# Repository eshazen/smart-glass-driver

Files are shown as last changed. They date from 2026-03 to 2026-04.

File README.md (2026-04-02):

# smart-glass-driver

This is a line-powered programmable function generator capable
of generating an output of about 140V pk-pk on each of two outputs
(which can be out of phase).

Here are the specs from Darren:

1.  Provide amplitude up to about 60-70Vpp AC (note: not 60 VAC RMS),
    we need to be able to change the amplitude for testing, with
    likely voltages 20, 30, 40, 50, 60 VppAC
2.  We also need to be able to alter the AC frequency, from low Hz to
    up to at least 1 kHz.
3.  We need to be able to have control over the output, with the
    ability to modulate (binary turn on and off) the output signal
    from a few Hz to up to about 300Hz. We would use this for
    lock-in. I envision control with a digital I/O pin.

For 1kHz sine wave with ~16 samples per cycle, the sampling rate would
be 62.5us or for 8 samples 125us.  

We need to stop Timer0 to avoid the interrupts.  Use TimerOne library
to interrupt at 62us and take values from a table.  This seems to
work just fine.  **But** we need to do two channels
out of phase on two DACs.  Simulate this with Set1 and Set2 functions.

The slew rate of the LTC6090 is spec'd at 21V/us.  So for 120V this
would be about 6uS or a minimum cycle time of 12uS 80kHz so no problem
reproducing a 1kHz output.  This is well matched to the 5us slew of
the DAC.

## 2026-04-02

ECOs for "Eric's" board:

*  Solder a wire between pins 1 and 6 of U1 (best done on the bottom side)
This connects DAC reference to 5V
*  Solder a wire between J4 pin 3 and J2 pin 5
*  Solder a wire between J4 pin 4 and J2 pin 7.
This connects the SPI data and clock to the right Arduino pins

## 2026-04-01

Ordered parts to assemble a system based on a transformer-based zener supply
and two InTENS shield boards.

Investigating the MCP492x DAC using the BE511 shield board.
<br>DAC setting code for first test:

```
    // Write a word to DAC channel 0 only
    // Unbuffered mode so no need to manipulate LDAC
    void MCP4922::Set1( int A) {
      int channelA = A | 0b0011000000000000; // unbuffered mode, gain = 2X
      SPI.beginTransaction(SPISettings(MCP_CLOCK, MSBFIRST, SPI_MODE0));
      digitalWrite(_CS, LOW);
      SPI.transfer(highByte(channelA));
      SPI.transfer(lowByte(channelA));
      digitalWrite(_CS, HIGH);
      SPI.endTransaction();
    }
```

On an Uno R3 with SPI clk set to 8MHz this takes 17us (plus any timer
interrupt delay).  Also the DAC takes 5us to slew full scale (roughly
linear).

**Software Written**: sketch `DAC_Function_Gen` accepts integer rates
from 25-2000 Hz (more or less, up to 1kHz best).  Serial at 9600.

## 2026-03-31

### Testing the commercial setup

Made some measurements of the commercial driver with Weizhe.
General observations:

* Drive electronics supplied provides about 200V pk-pk AC
two-phase at 60Hz.  Not quite sinusoidal.
* Tested with 4.7k resistor in series.  Current waveform
is roughly in phase with voltage.  Amplitude is about 2mA (absolute value).

### Testing Amazon HV supply

Now testing an HV supply I found in the box with the InTENS stuff.

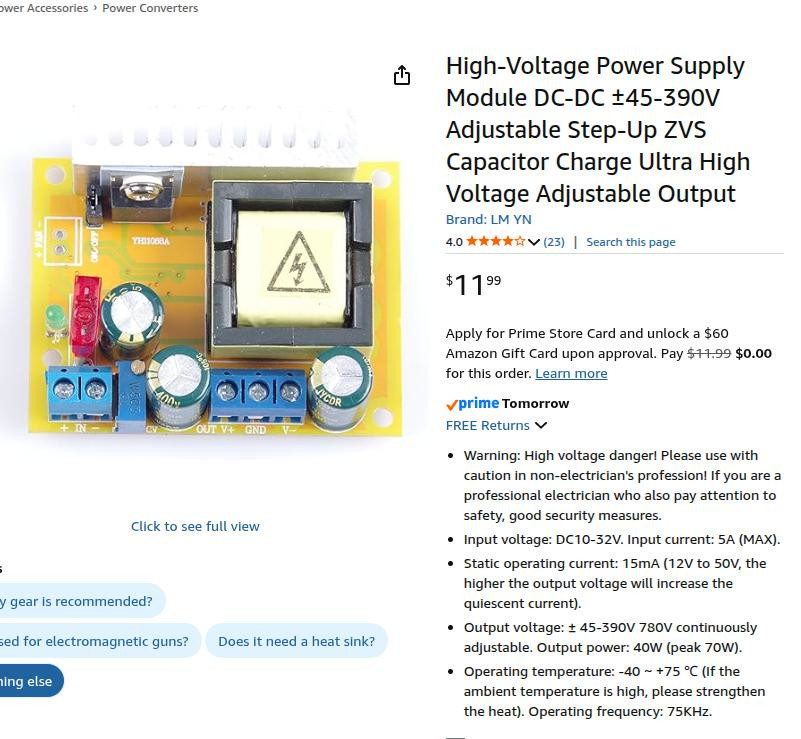
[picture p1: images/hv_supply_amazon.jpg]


It claims to deliver up to 40W or 15mA.  

* Test with 47k load.  Get a pretty nasty ripple of 20V @ 10Hz.
* Test with 22k load.  Just as bad.

Probably not worth considering using this thing.

### Considering home-made supply

We could build a nice +/-65V supply using a Triad N-68X transformer,
bridge rectifier and an RC filter with zener regulator.

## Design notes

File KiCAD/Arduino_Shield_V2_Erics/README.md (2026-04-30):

This is the "as built" shield design from InTENS.
(boards with blue soldermask).

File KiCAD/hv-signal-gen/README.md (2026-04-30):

# hv-signal-gen

As of 5/26 this design has not been built.
It serves as a reference for the power supply schematic.

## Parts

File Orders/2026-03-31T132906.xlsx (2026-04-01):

Digi-Key: Shopping Cart
Index | Quantity | Part Number | Manufacturer Part Number | Description | Customer Reference | Available | Backorder | Unit Price | Extended Price USD
1 | 4 | MCP4921-E/P-ND | MCP4921-E/P | IC DAC 12BIT V-OUT 8DIP |  | 4 | 0 | 2.81 | 11.24
2 | 4 | 505-LTC6090CS8E#TRPBFCT-ND | LTC6090CS8E#TRPBF | IC OPAMP GP 1 CIRCUIT 8SOIC |  | 4 | 0 | 10.68 | 42.72
3 | 4 | SSQ-106-24-G-S-ND | SSQ-106-24-G-S | CONN RCPT 6POS 0.1 GOLD PCB |  | 4 | 0 | 1.93 | 7.72
4 | 8 | SSW-108-04-G-S-ND | SSW-108-04-G-S | CONN RCPT 8POS 0.1 GOLD PCB |  | 8 | 0 | 2.04 | 16.32
5 | 4 | SSW-110-04-G-S-ND | SSW-110-04-G-S | CONN RCPT 10POS 0.1 GOLD PCB |  | 4 | 0 | 2.54 | 10.16
6 | 2 | 237-1624-ND | N-68X | XFRMR ISOL 115V 230V-115V 50VA |  | 2 | 0 | 17.73 | 35.46
7 | 2 | KBP06G-ND | KBP06G | BRIDGE RECT 1PHASE 600V 1.5A KBP |  | 2 | 0 | 0.82 | 1.64
8 | 5 | 100AUCT-ND | FKN2WSJT-73-100R | RES 100 OHM 5% 2W AXIAL |  | 5 | 0 | 0.14 | 0.70
9 | 4 | 565-EKXJ251ELL101MK30S-ND | EKXJ251ELL101MK30S | CAP ALUM 100UF 20% 250V RADIAL |  | 4 | 0 | 1.57 | 6.28
10 | 5 | 399-ESK226M100AE3AA-ND | ESK226M100AE3AA | CAP ALUM 22UF 20% 100V RADIAL TH |  | 5 | 0 | 0.26 | 1.30
11 | 5 | 4878-ZY68-ND | ZY68 | DIODE ZENER 68V 2W DO204AC |  | 5 | 0 | 0.35 | 1.75
12 | 2 | 5410-R-3013S(01)-ND | R-3013S(01) | PWR ENT MOD RCPT IEC320-C14 + SW |  | 2 | 0 | 4.27 | 8.54
13 | 4 | DKS-SOLDERBREAD-01-ND | DKS-SOLDERBREAD-01 | BREADBOARD GENERAL PURPOSE PTH |  | 4 | 0 | 2.49 | 9.96

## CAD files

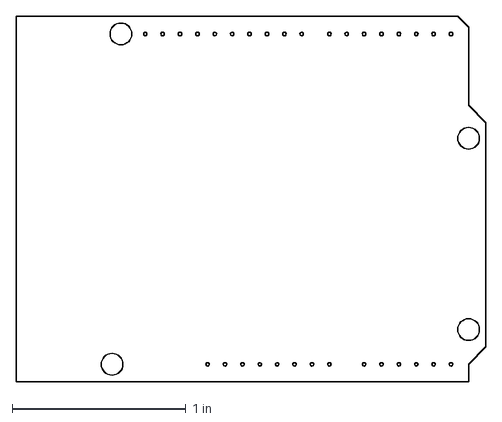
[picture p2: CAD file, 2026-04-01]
3D/Arduino UNO R3 shield - full.dxf
2.70 x 2.10 in

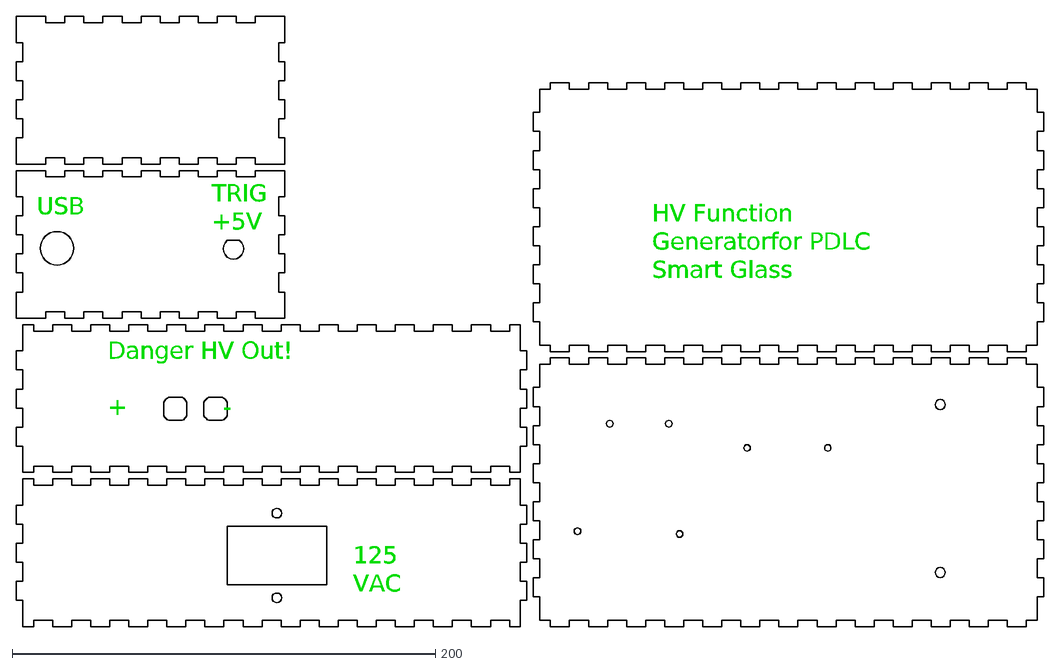
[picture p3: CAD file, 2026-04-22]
3D/box_v2.dxf
Danger HV Out! + -
USB
125 VAC
HV Function Generator for PDLC Smart Glass
TRIG +5V

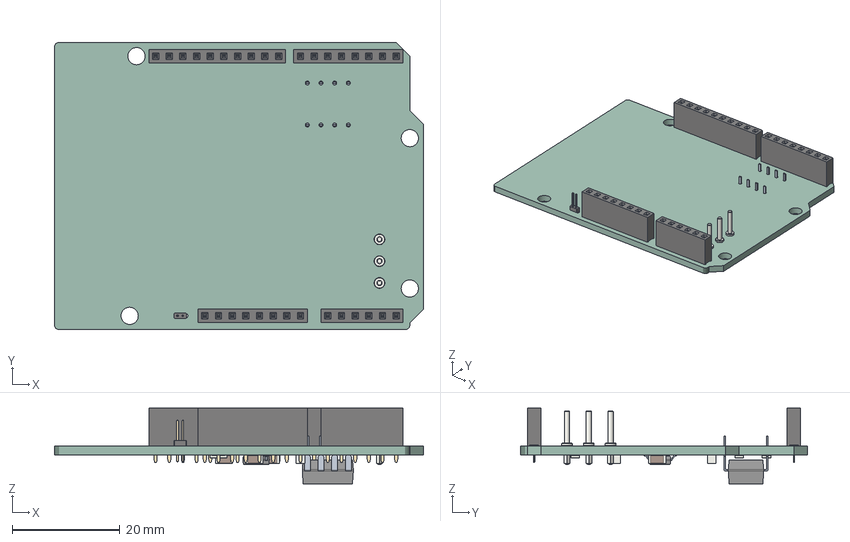
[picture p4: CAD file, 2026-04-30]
KiCAD/Arduino_Shield_V2_Erics/PCB.step
68.6 x 53.3 x 14.0 mm
PCB PCB

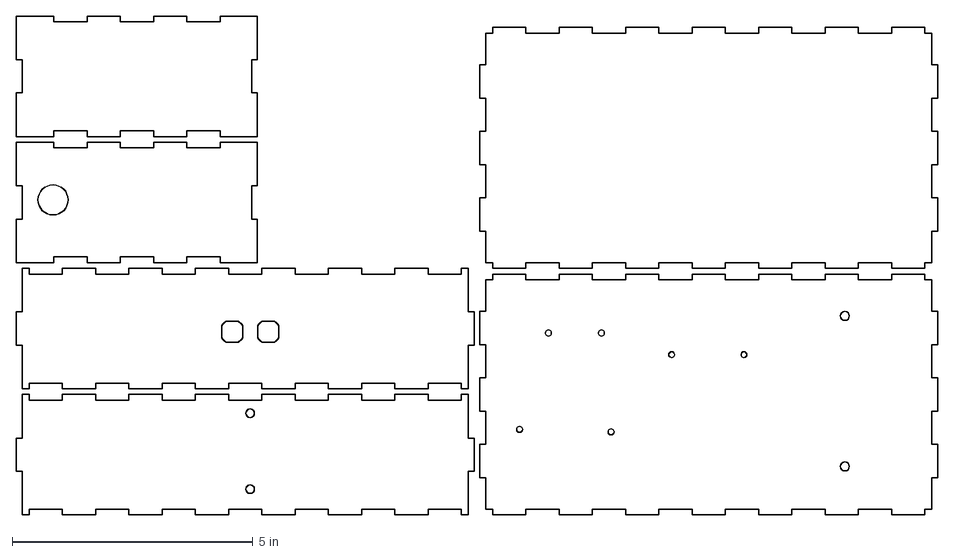
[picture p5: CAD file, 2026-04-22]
3D/#hv_box.dxf
19.1 x 10.4 in

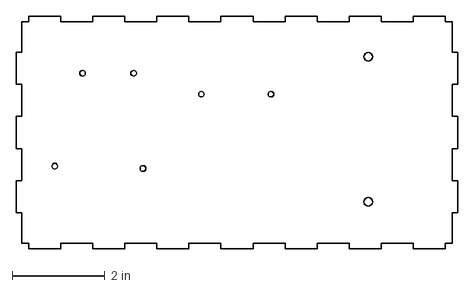
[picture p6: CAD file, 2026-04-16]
3D/hv_bottom.dxf
9.50 x 5.00 in

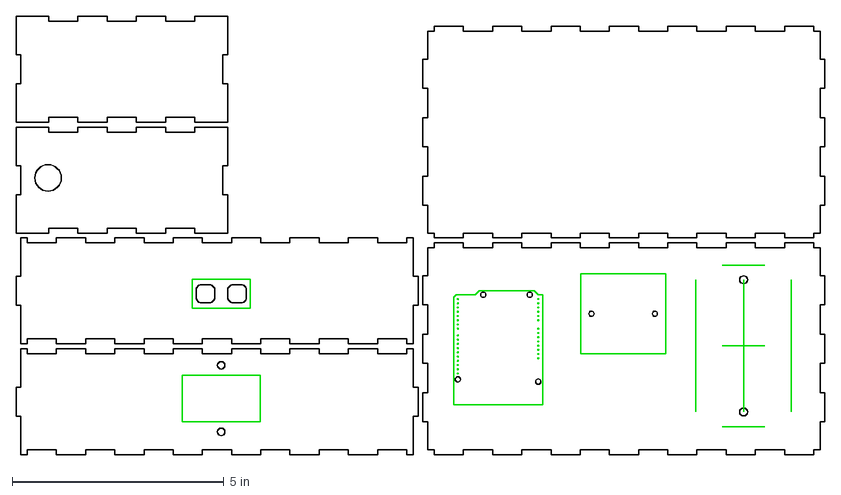
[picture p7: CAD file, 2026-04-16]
3D/#mounting_plate.dxf
19.1 x 10.4 in

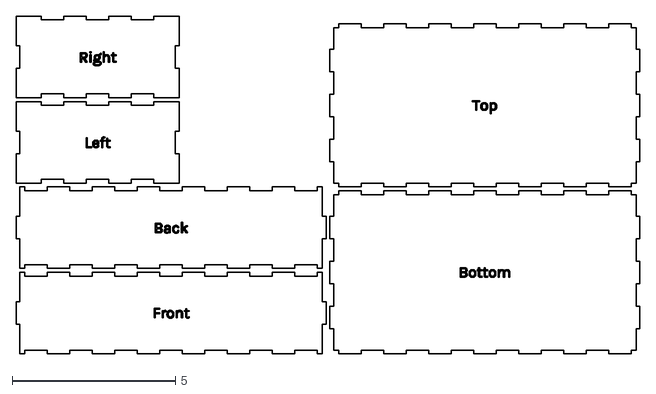
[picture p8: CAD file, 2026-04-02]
3D/box.dxf
19.1 x 10.4

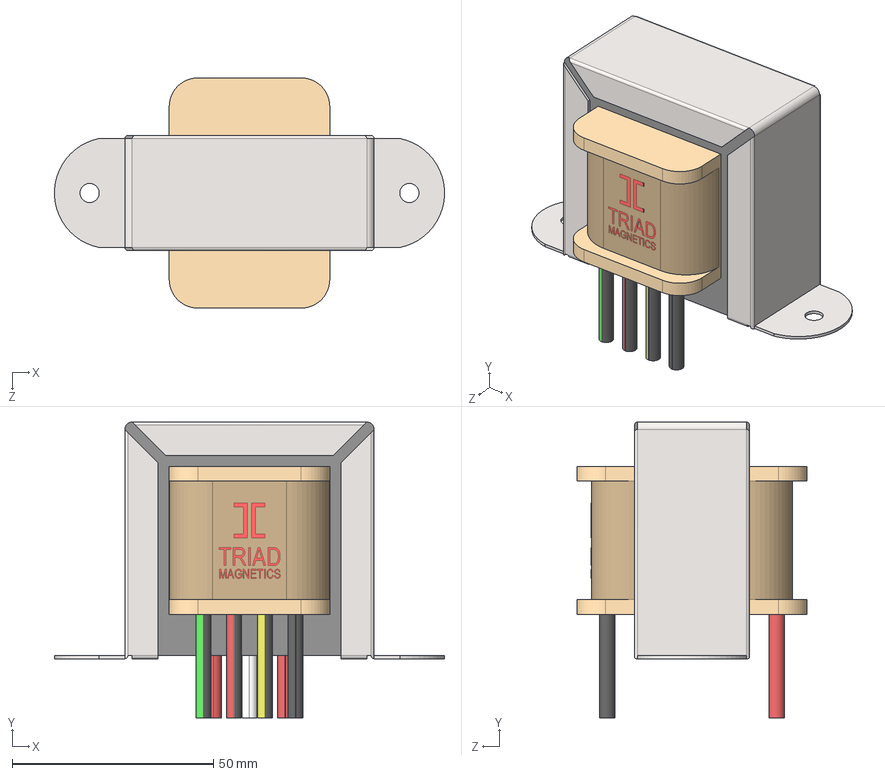
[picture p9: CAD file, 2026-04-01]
3D/N-68X.STEP
96.8 x 73.4 x 57.1 mm

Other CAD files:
3D/hv_box.dxf
3D/mounting_plate.dxf

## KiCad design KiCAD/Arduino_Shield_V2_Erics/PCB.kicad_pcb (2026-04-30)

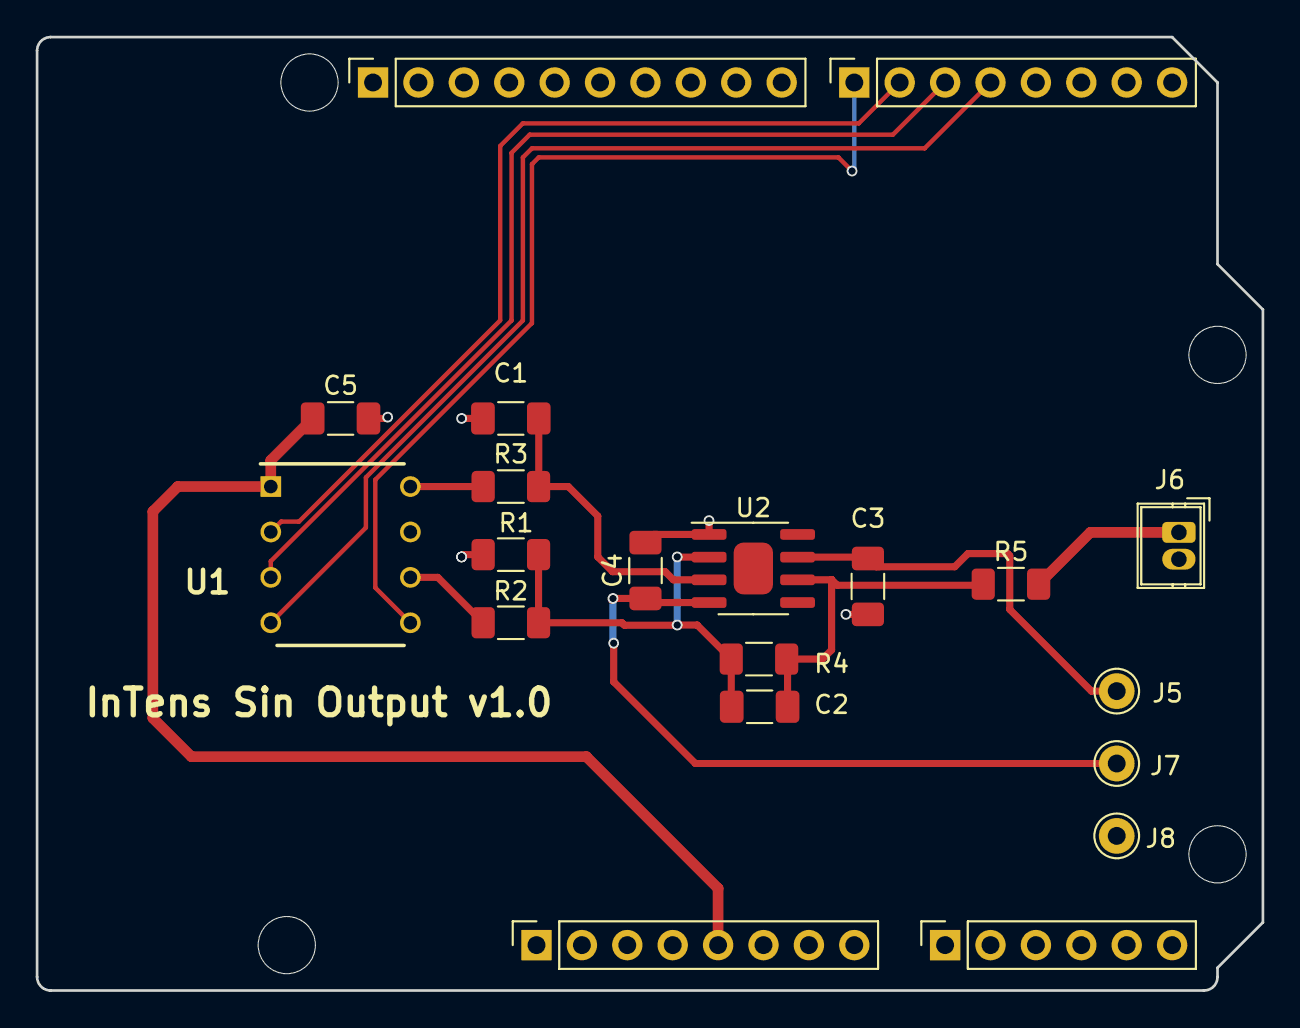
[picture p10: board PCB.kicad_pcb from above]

Board: 2 copper layers, 68.6 x 53.3 mm, 24 parts (0 on the bottom side), 17 nets.

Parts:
C1: 470pF; C_1206_3216Metric_Pad1.33x1.80mm_HandSolder
C2: 10pF; C_1206_3216Metric_Pad1.33x1.80mm_HandSolder
C3, C4: 0.1uF; C_1206_3216Metric_Pad1.33x1.80mm_HandSolder
C5: 0.1 uF; C_1206_3216Metric_Pad1.33x1.80mm_HandSolder
J1: Power; PinSocket_1x08_P2.54mm_Vertical
J2: Digital/PWM; PinSocket_1x10_P2.54mm_Vertical
J3: Analog; PinSocket_1x06_P2.54mm_Vertical
J4: Digital/PWM; PinSocket_1x08_P2.54mm_Vertical
J5, J7, J8: Conn_01x01; Pin_D1.0mm_L10.0mm
J6: Conn_01x01_Socket; Wuerth_WR-WTB_64800211622_1x02_P1.50mm_Vertical
MH1, MH2, MH3, MH4: MountingHole_3.2mm
R1: 16.2kΩ; R_1206_3216Metric_Pad1.30x1.75mm_HandSolder
R2: 16.9kΩ; R_1206_3216Metric_Pad1.30x1.75mm_HandSolder
R3: 10kΩ; R_1206_3216Metric_Pad1.30x1.75mm_HandSolder
R4: 453kΩ; R_1206_3216Metric_Pad1.30x1.75mm_HandSolder
R5: 40kΩ; R_1206_3216Metric_Pad1.30x1.75mm_HandSolder
U1: MCP4921; DIP781W56P254L950H533Q8N
U2: LTC6090; SOIC-8-1EP_3.9x4.9mm_P1.27mm_EP2.29x3mm

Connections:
+5V: C5.1, J1.5, U1.1 (Vdd)
-VSW: C4.1, J7.1, U2.4
/4: J4.4, U1.4 (SDI)
/7: J4.1, U1.5 (~LDAC)
/*5: J4.3, U1.3 (SCK)
/*6: J4.2, U1.2 (~CS)
/HV_OA: C2.2, R4.2, R5.1, U2.6
/HV_OUT: J6.1, R5.2
/SCL/A5: J2.1, J3.6
/SDA/A4: J2.2, J3.5
GND: C1.2, C3.2, C4.2, C5.2, J1.6, J1.7, J2.4, J6.2, J8.1, R2.1, U1.7 (Vss), U2.1
HT: C3.1, J5.1, U2.7
unnamed: C1.1, R3.2, U2.3
unnamed: C2.1, R1.1, R2.2, R4.1, U2.2
unnamed: R3.1, U1.8 (Vout)
unnamed: R1.2, U1.6 (Vref)
unnamed: U2.5, U2.8

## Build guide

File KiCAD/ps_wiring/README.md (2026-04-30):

# ps-wiring

This is the current design for the power supply.
Tested and working... provides +/-70V at no load.

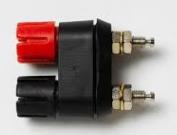
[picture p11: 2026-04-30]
Wiring/binding-post.png

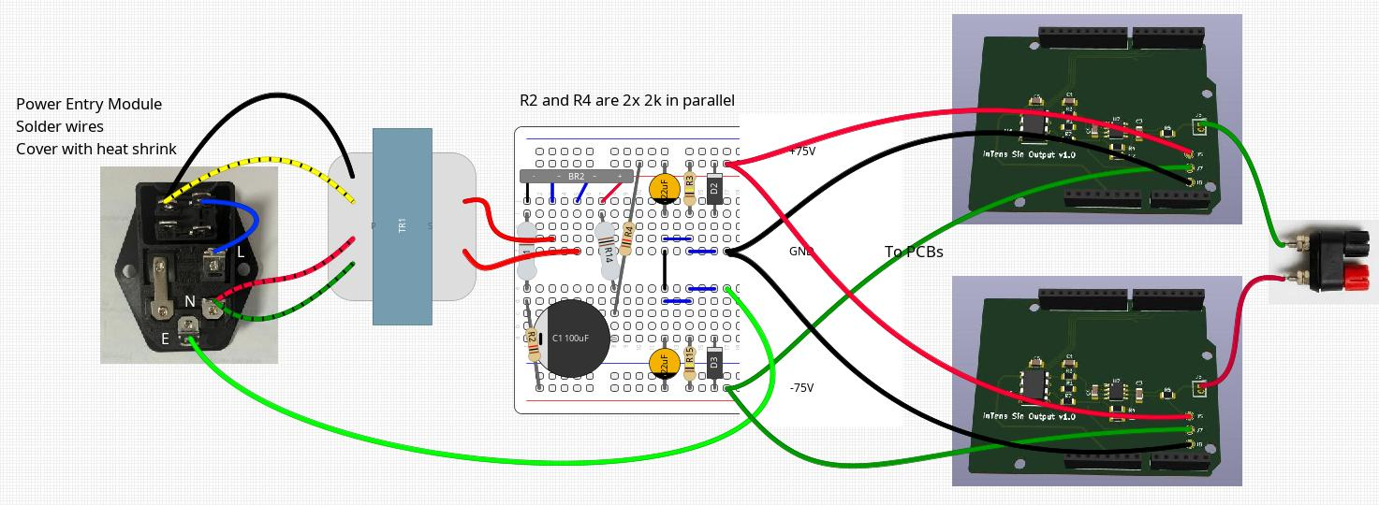
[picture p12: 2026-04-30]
Wiring/wiring.png

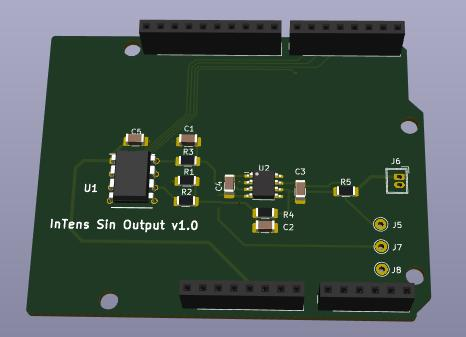
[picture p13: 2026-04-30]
Wiring/pcb_image.png

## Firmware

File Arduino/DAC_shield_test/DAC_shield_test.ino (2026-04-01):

//
// Eric's ADC and DAC test code for Arduino shield
//

// these are pinouts for analog shield on Arduino with an Uno R3
#define DAC_SDI 11
#define DAC_SCK 13
#define DAC_CS 9
#define DAC_LDAC 7
#define DAC_SHDN 6

#include <TimerOne.h>
// #include "MCP320x.h"
#include "MCP4922.h"
#include "SineTable.h"
#include <SPI.h>

#define USE_ISR

// MCP320x MYADC(ADC_CS_PIN);
MCP4922 MYDAC( DAC_SDI, DAC_SCK, DAC_CS, DAC_LDAC);

volatile int dac_values[] = {0, 2047, 4095, 2047};
#define NDAC (sizeof(dac_values)/sizeof(dac_values[0]))
volatile int nsamp = 0;

void DAC_ISR(void) {
  MYDAC.Set1(dac_values[nsamp]);
  MYDAC.Set2(4095-dac_values[nsamp]);
  ++nsamp;
  if( nsamp >= NDAC)
    nsamp = 0;
}

void setup() {
  SPI.begin();
  pinMode( DAC_SHDN, OUTPUT);
  digitalWrite( DAC_SHDN, HIGH);

  TCCR0B = 0;			// stop timer 0

  // try to set up timer 1 for interrupts at 125us)
#ifdef USE_ISR
  Timer1.initialize(PERIOD_US);
  Timer1.attachInterrupt(DAC_ISR);
  Timer1.start();
#endif
}

void loop() {
#ifdef USE_ISR
  ;
#else
  DAC_ISR();
#endif  
}

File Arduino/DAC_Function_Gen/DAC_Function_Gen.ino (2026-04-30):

//
// Function generator for smart glass driver
//
// Generate sine waves from 10-1000 Hz
//
// Commands:
// h           - help
// f frq amp   - run continuous frq in Hz, amplitude / 2047
//

// output pins for InTENS board with MCP4921
#define DAC_LDAC 7

#define DAC_SDI 11
#define DAC_SCK 13

#define DAC_CS1 6
#define DAC_CS2 8

#include <TimerOne.h>
// #include "MCP320x.h"
#include "MCP4922.h"
#include "SineTable.h"
#include <SPI.h>

#define USE_ISR

// DAC 1
MCP4922 MYDAC1( DAC_SDI, DAC_SCK, DAC_CS1, DAC_LDAC);
MCP4922 MYDAC2( DAC_SDI, DAC_SCK, DAC_CS2, DAC_LDAC);

// NOTE:  if memory is tight/full, reduce size of samples[]
volatile int samples[500] = {2047, 2047};
#define MSAMP (sizeof(samples)/sizeof(samples[0]))
volatile int nsamp = 2;		// maximum sample# in samples[]
volatile int csamp = 0;		// current sample# in samples[]

void DAC_ISR(void) {
  MYDAC1.Set1(samples[csamp]);
  MYDAC2.Set1(4095-samples[csamp]);
  ++csamp;
  if( csamp >= nsamp)
    csamp = 0;
}

void setup() {
  Serial.begin(9600);
  Serial.setTimeout(100000);
  while( !Serial)
    ;

  Serial.println("SG 1.0");

  SPI.begin();
#ifdef DAC_SHDN
  pinMode( DAC_SHDN, OUTPUT);
  digitalWrite( DAC_SHDN, HIGH);
#endif

  TCCR0B = 0;			// stop timer 0

  // try to set up timer 1 for interrupts at PERIOD_US us (from SineTable.h)
#ifdef USE_ISR
  Timer1.initialize(PERIOD_US);
  Timer1.attachInterrupt(DAC_ISR);
  Timer1.start();
#endif
}

// maximum number of command arguments to parse
#define MAXARG 5

// these are global so they are included in the report of variable size use
static char buff[80];
static char* argv[MAXARG];
static unsigned iargv[MAXARG];

static int rate;
static int ampl;
static int rc;

void loop() {

  // send a prompt, wait for it to be transmitted
  Serial.write(">");    
  Serial.flush();
  
  // read a ststring into buff with editing
  my_gets( buff, sizeof(buff));

  // parse into text and integer tokens (see parse.ino)
  int argc = parse( buff, argv, iargv, MAXARG);

  switch( toupper( *argv[0])) {
  case 'H':
    Serial.println( "Commands:");
    Serial.println( "h    - help");
    Serial.println( "f <freq> <amp>");
    Serial.println( "  <freq> is frequency in Hz.  Note that DAC is updated every 50us");
    Serial.println( "  <amp> is amplitude 0-2047");

    break;

  case 'F':
    rate = iargv[1];
    ampl = iargv[2];

    rc = SineTable( rate, ampl, (int *)samples, MSAMP);
    if( rc > 0)
      nsamp = rc;
    break;

  default:
    Serial.print("Unknown command: ");
    Serial.println( *argv[0]);
  }

}

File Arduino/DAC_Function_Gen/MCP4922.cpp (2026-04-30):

/*******************************************************************************
*  MCP4922.cpp - Library for driving MCP4922 2 channel DAC using hardware SPI. *
* Created by Helge Nodland, January 1, 2015.
* 
* Released into the public domain.                                             *
*******************************************************************************/

#if defined(ARDUINO) && ARDUINO >= 100
#include "Arduino.h"
#else
#include "WProgram.h"
#endif

#include "MCP4922.h"
#include <SPI.h>

#define MCP_CLOCK			8000000UL	      // 8MHz clock rate

#define BUFFERED_DAC

MCP4922::MCP4922(int SDI, int SCK, int CS, int LDAC)
{
 _SDI = SDI;
 _SCK = SCK;
 _CS = CS;
 _LDAC = LDAC;

 pinMode(_SDI,OUTPUT);
 pinMode(_SCK,OUTPUT);
 pinMode(_CS,OUTPUT);
 pinMode(_LDAC,OUTPUT);

}

//************************************************************************
void MCP4922::Set(int A, int B) {
  sendIntValueSPI(A,B);
}

// Write a word to DAC channel 0 only
// Unbuffered mode so no need to manipulate LDAC
void MCP4922::Set1( int A) {
#ifdef BUFFERED_DAC
  int channelA = A | 0b0111000000000000; // buffered mode, gain = 2X
#else
  int channelA = A | 0b0011000000000000; // unbuffered mode, gain = 2X
#endif
  SPI.beginTransaction(SPISettings(MCP_CLOCK, MSBFIRST, SPI_MODE0));
  digitalWrite(_CS, LOW);
  SPI.transfer(highByte(channelA));
  SPI.transfer(lowByte(channelA));
  digitalWrite(_CS, HIGH);
#ifdef BUFFERED_DAC1
  digitalWrite(_LDAC,LOW);
  SPI.endTransaction();
  __asm__("nop\n\t");
  digitalWrite(_LDAC,HIGH);
#else  
  SPI.endTransaction();
#endif
}

// Write a word to DAC channel 1 only
// Unbuffered mode so no need to manipulate LDAC
void MCP4922::Set2( int A) {
  int channelA = A | 0b1011000000000000; // unbuffered mode, gain = 2X
  SPI.beginTransaction(SPISettings(MCP_CLOCK, MSBFIRST, SPI_MODE0));
  digitalWrite(_CS, LOW);
  SPI.transfer(highByte(channelA));
  SPI.transfer(lowByte(channelA));
  digitalWrite(_CS, HIGH);
#ifdef BUFFERED_DAC
  digitalWrite(_LDAC,LOW);
  SPI.endTransaction();
  __asm__("nop\n\t");
  digitalWrite(_LDAC,HIGH);
#else  
  SPI.endTransaction();
#endif
}

//************************************************************************ 
/*
Bitmasking for setting options in dac:

The four MSB in the Mask 0b0111000000000000 and 0b1111000000000000 is for
setting different options of the DAC setup.

0bX111000000000000 where X is What DAC channel the SPI is writing to.
bit15			   X=0 is writing to channel A.
				   X=1 is writing to channel B.

0b0X11000000000000 where X is Buffered or UnBuffered mode. Buffered uses LDAC 
bit14			   pin to simuttaneous update both channels.
				   UnBuffered I guess is writing outputs directly to DAC 
				   outputs and ignoring LDAC pin.
				   X=0 is UnBuffered.
				   X=1 is Buffered.
				   
0b01x1000000000000 where X is GAIN selector.  
bit13			   X=0 is 2X GAIN.
				   X=1 is 1X GAIN.
				   
0b011X000000000000 where X SHUTDOWN.
bit12			   X=0 OUTPUT is DISABLED on selected channel.
				   X=1 OUTPUT is ENABLED on selected channel.
			
0b0111XXXXXXXXXXXX where X is the 12 bits to be written to the active channel.
bit 11 down to bit 0			

 */
//************************************************************************

void MCP4922::sendIntValueSPI(int A ,int B) {
int channelA = A | 0b0111000000000000;
int channelB = B | 0b1111000000000000;
       
SPI.beginTransaction(SPISettings(MCP_CLOCK, MSBFIRST, SPI_MODE0));		// use highest clock allowed for 3.3V operation
digitalWrite(_CS, LOW);
SPI.transfer(highByte(channelA));
SPI.transfer(lowByte(channelA));
digitalWrite(_CS, HIGH);
SPI.endTransaction();

__asm__("nop\n\t");
//delay(1);

SPI.beginTransaction(SPISettings(MCP_CLOCK, MSBFIRST, SPI_MODE0));		// use highest clock allowed for 3.3V operation
digitalWrite(_CS, LOW);
SPI.transfer(highByte(channelB));
SPI.transfer(lowByte(channelB));
digitalWrite(_CS, HIGH); 
digitalWrite(_LDAC,LOW);
SPI.endTransaction();

__asm__("nop\n\t");
//delay(1);

digitalWrite(_LDAC,HIGH);
} 
 
 

 

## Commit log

2026-03-25 starting on schematic
    [hv-signal-gen.kicad_pcb, hv-signal-gen.kicad_sch, hv_dac.kicad_sch]
2026-04-01 initial software
    [2026-03-31T132906.xlsx, Arduino UNO R3 shield - full.dxf, N-68X.STEP, hv-signal-gen.kicad_sch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]
2026-04-16 box and wiring
    [#mounting_plate.dxf, hv_bottom.dxf, hv_box.dxf, hv_dac.kicad_sch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]
2026-04-22 update box, wiring
    [#hv_box.dxf, box_v2.dxf]
2026-04-23 DAC_Function_Gen working on one board
2026-04-30 update DIY drawing
    [PCB-B_Cu.gbr, PCB-B_Mask.gbr, PCB-B_Silkscreen.gbr, PCB-Edge_Cuts.gbr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]
2026-04-30 Update documentation
    [PCB.kicad_sch]
2026-04-30 Schematic notes; initial software working
    [PCB.kicad_sch]
